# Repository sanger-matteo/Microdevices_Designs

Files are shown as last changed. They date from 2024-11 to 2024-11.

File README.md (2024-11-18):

This repository contains a collection of files used for the creation of microfluidic masks and photolithography work.

## Description of files
This repository includes several scripts used in the study. Below is a brief overview of each:
- **Lithography - Fabrication protocols**:
	- Contains files with different protocols used for the treatment of Si-wafers, photoresist, and fabrication processes for photolithography of microfluidic molds
- **Mask Designs**: if the file are not metric unit, assume *1 unit = 1 micrometer*
	- *Designs:* the *.dwg* and *.dxf* files drawn in CAD that outline the design of different microfluidic designs 
	- *Orders:* similar to "Deasigns", it contains the final *.dwg* and *.dxf* designed used to order and print photolithographhy masks (mostly negative).
- **3D_Nanolithography:**
	- It contains both the *.dwg* and *.stl* of microfluidic molds created via 3D-printing nanolithography.

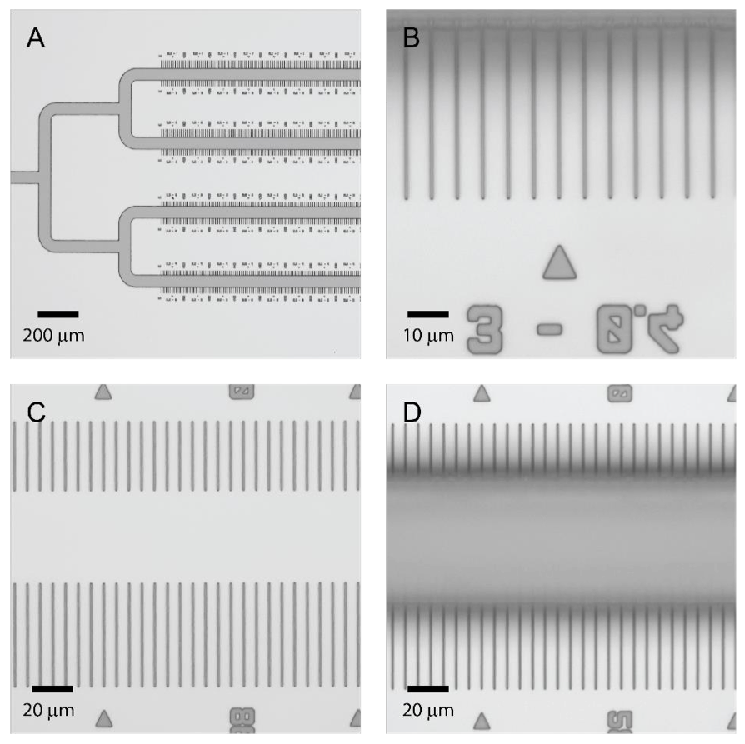
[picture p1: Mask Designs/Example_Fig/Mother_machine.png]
|  |
|---|
| Example 1 - Mother machine Si-Photoresist mold |

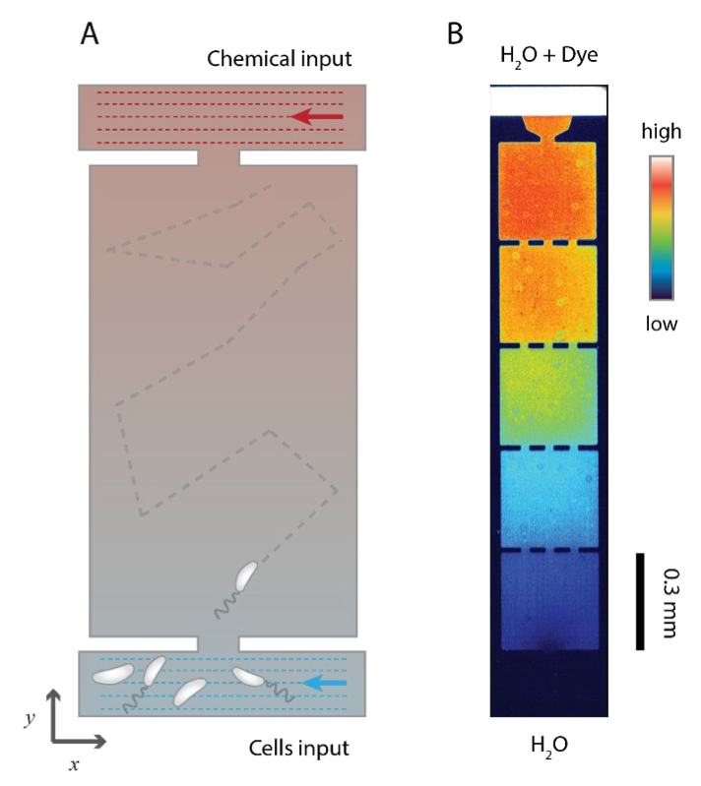
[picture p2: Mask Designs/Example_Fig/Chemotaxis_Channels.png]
|  
|--- |
| Example 2 - Schematic example of a chemotaxis chamber and false color microscopy image of the diffusion and gradient formation of fluorescently labelled molecules |

Some of these files were associated with the following papers (the rest were unpublished or contributed to minor/external collaborations):  
- [Tad Pili Play a Dynamic Role in Caulobacter crescentus Surface Colonization](https://doi.org/10.1128/mbio.01237-19)
- [A Surface-Induced Asymmetric Program Promotes Tissue Colonization by Pseudomonas aeruginosa](https://doi.org/10.1016/j.chom.2018.11.008)
- [Bacteria-on-a-bead: probing the hydrodynamic interplay of dynamic cell appendages during cell separation](https://doi.org/10.1038/s42003-022-04026-z)
- [In situ structure of the Caulobacter crescentus flagellar motor and visualization of binding of a CheY-homolog]( https://doi.org/10.1111/mmi.14525)

Some more specifics can be found in the [thesis](https://edoc.unibas.ch/65308/1/Thesis_v11_edoc.pdf) manuscript.

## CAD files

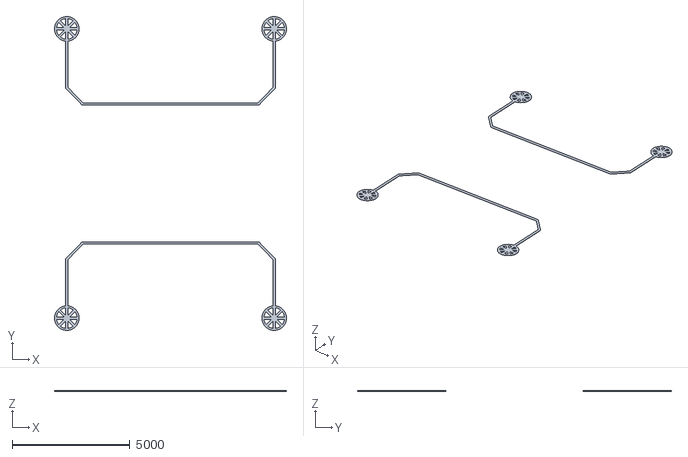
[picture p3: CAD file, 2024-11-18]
Mask Designs/3D_Nanolithography/MGD_v1_channels_3D.stl
9851.3 x 13325.8 x 50.0

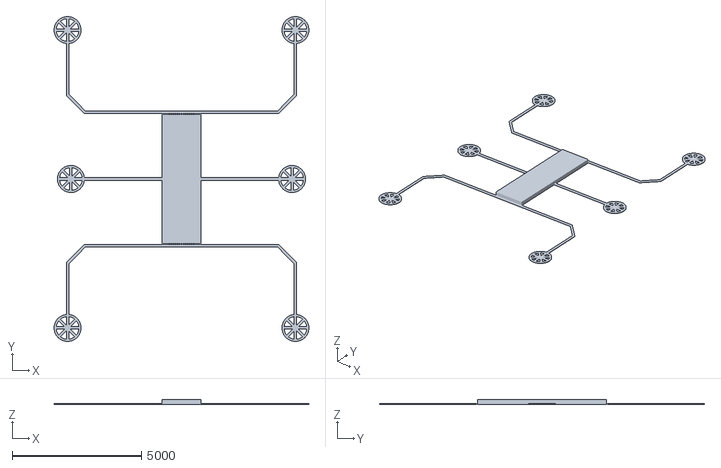
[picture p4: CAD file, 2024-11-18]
Mask Designs/3D_Nanolithography/GD_v1_3D.stl
9859.5 x 12567.7 x 200.0

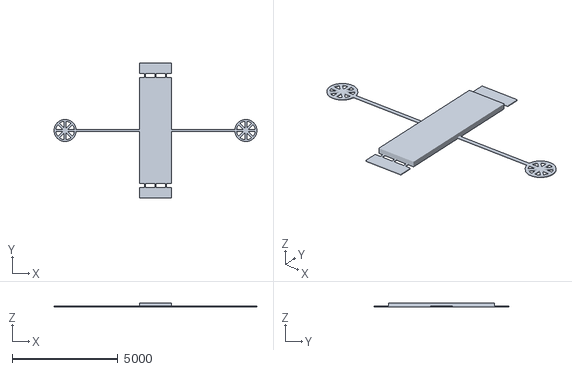
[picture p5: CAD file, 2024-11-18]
Mask Designs/3D_Nanolithography/MGD_v1_chamber_3D.stl
9600.0 x 6400.0 x 200.0

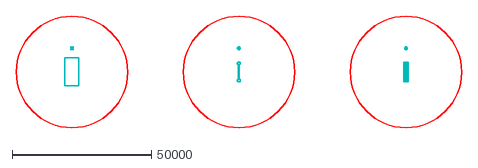
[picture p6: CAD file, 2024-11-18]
Mask Designs/Designs/141211 - MS 4 - Pressure Dev.dxf
160000.0 x 40000.0

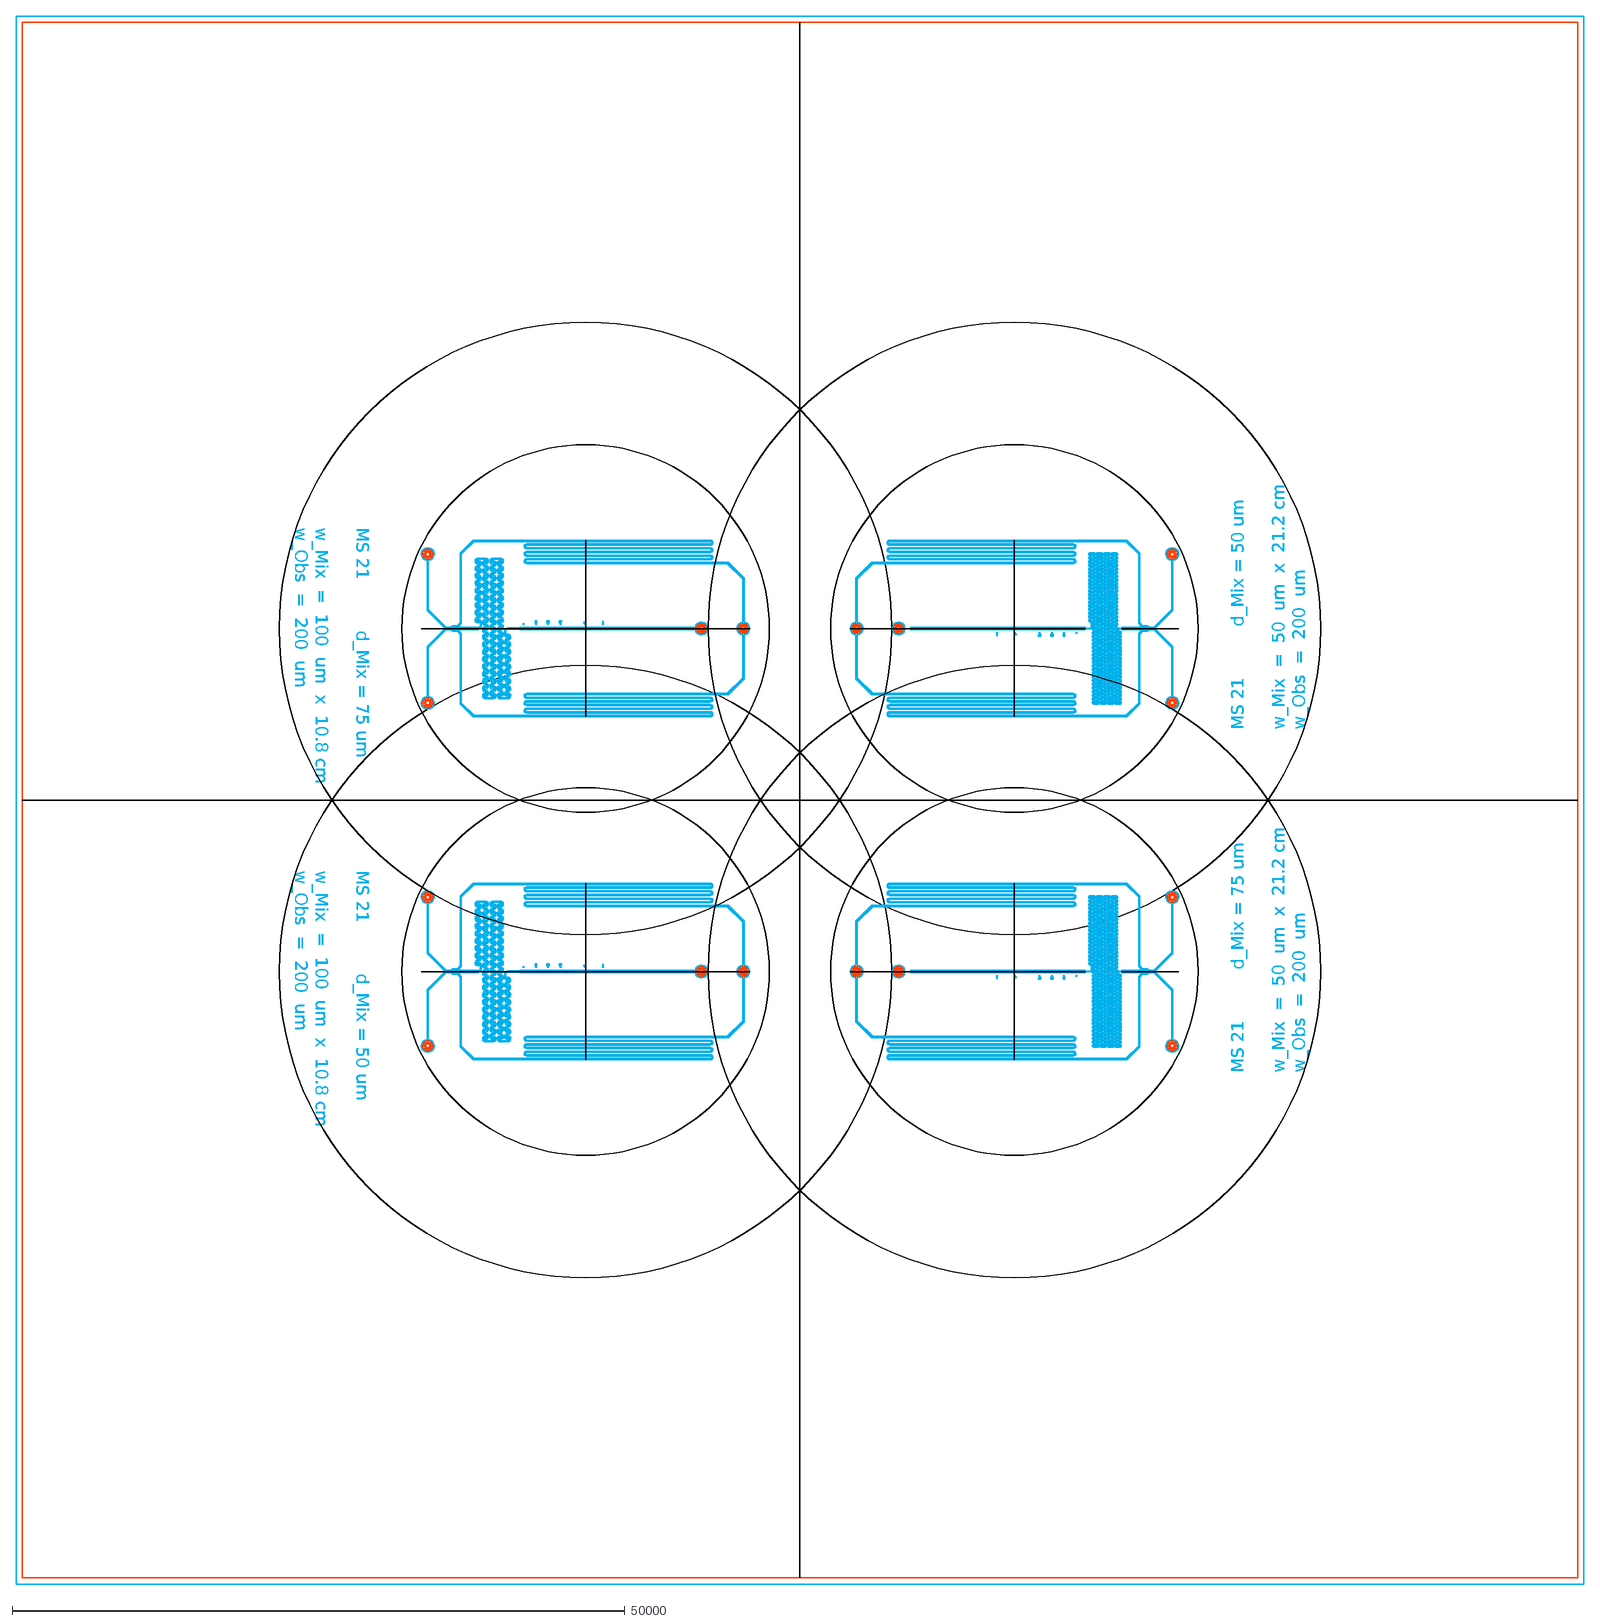
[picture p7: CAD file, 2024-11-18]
Mask Designs/Orders/171206 - Order MS 21 - Switch_Mix.dxf
MS 21 d_Mix = 50 um w_Mix = 100 um x 10.8 cm w_Obs = 200 um
MS 21 d_Mix = 75 um w_Mix = 100 um x 10.8 cm w_Obs = 200 um
MS 21 d_Mix = 50 um w_Mix = 50 um x 21.2 cm w_Obs = 200 um
MS 21 d_Mix = 75 um w_Mix = 50 um x 21.2 cm w_Obs = 200 um

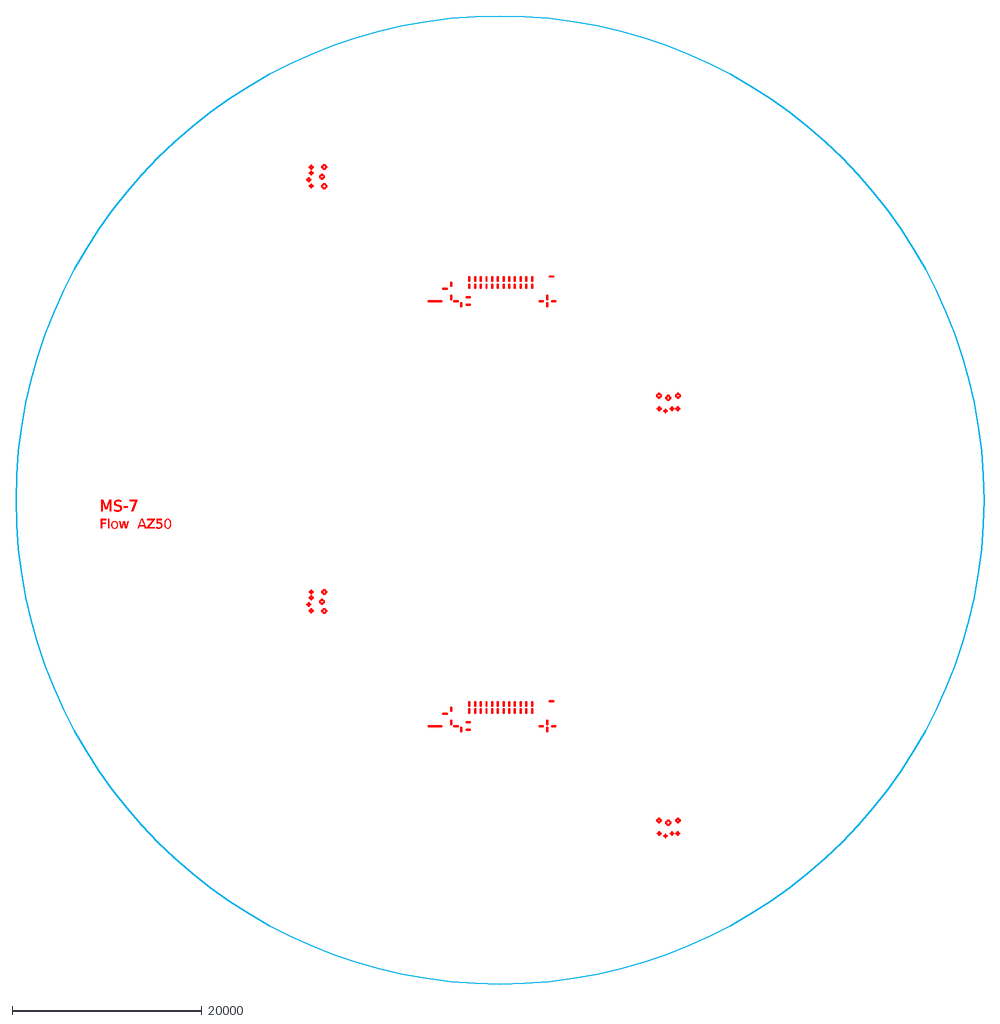
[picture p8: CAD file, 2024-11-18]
Mask Designs/Orders/150708 - Order MS-7 - 2 positive- UniBas - Sangermani.dxf
MS-7 Flow AZ50

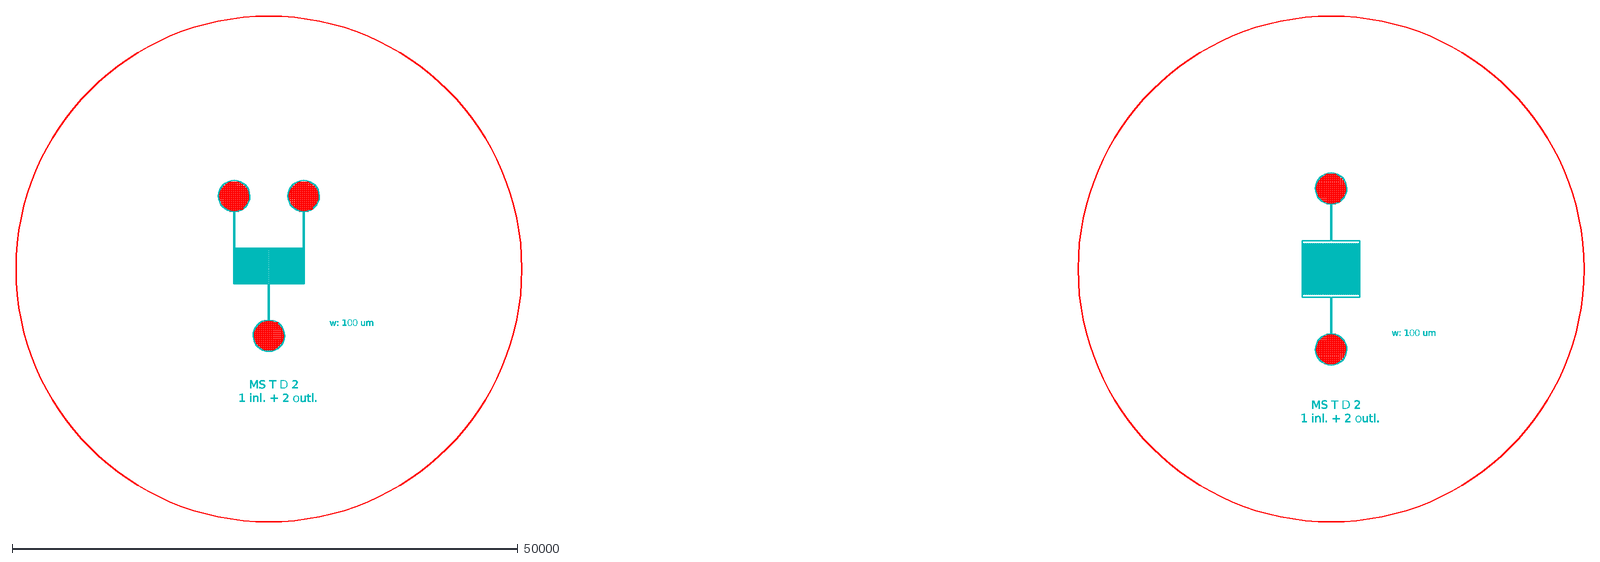
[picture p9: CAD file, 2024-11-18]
Mask Designs/Orders/141007 - Order MS 3 - UniBas - Sangermani.dxf
w: 100 um
MS T D 2 1 inl. + 2 outl.

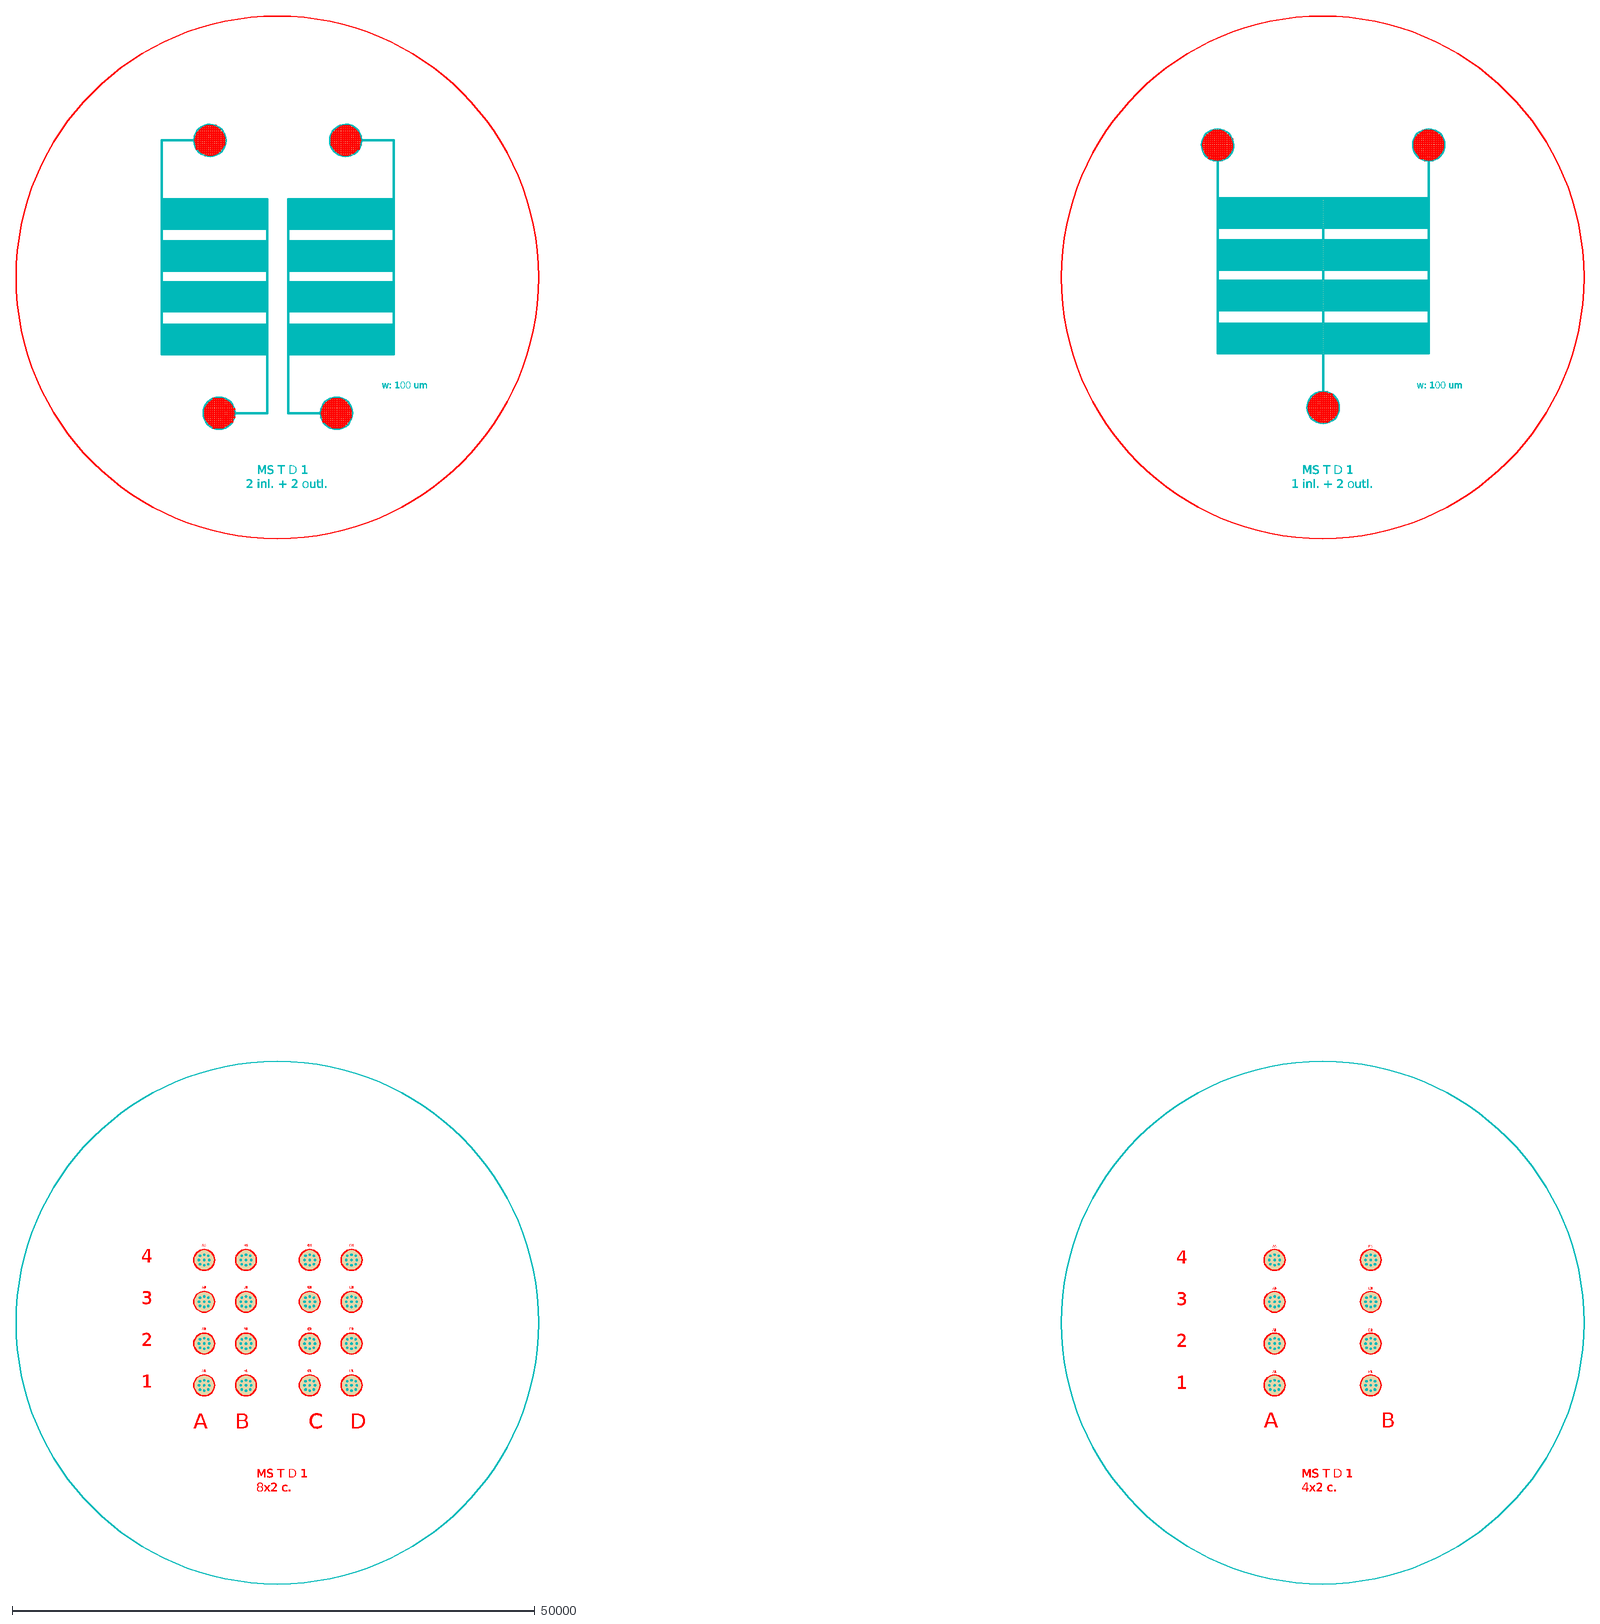
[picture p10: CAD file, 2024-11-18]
Mask Designs/Orders/140516 - Order MS 1 - UniBase - Sangermani.dxf
1
2
3
4
A
B
A1
A2
A3
A4
B4
B3
B2
B1
C
D
C1
C2
C3
C4
D4
D3
D2
D1
w: 100 um
MS T D 1 8x2 c.
MS T D 1 4x2 c.
MS T D 1 2 inl. + 2 outl.
MS T D 1 1 inl. + 2 outl.

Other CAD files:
Mask Designs/Orders/180709 - FW2_GDv2-4_MGDv1.dwg
Mask Designs/Designs/170628 - MS 17 - Switch_Flow_Channel.dwg
Mask Designs/Designs/160316 - MS 15 - Generation_Dev_1.dwg
Mask Designs/Orders/170111 - Order MS 16.2 - Mother Machine Caulo 2.dwg
Mask Designs/Designs/150811 - MS 9-12 - FAC-Counter.dwg
Mask Designs/Orders/160707 - Order MS 13-15 - Positive.dwg
Mask Designs/Designs/160316 - MS 13 - Pusher channel.dwg
Mask Designs/Designs/180704 - MothMach_3D - 2D.dwg
Mask Designs/Designs/171206 - MS 20 - Single_Layer_Valve.dwg
Mask Designs/3D_Nanolithography/GD_v1_3D.dwg
Mask Designs/3D_Nanolithography/MGD_v1_chamber_3D.dwg
Mask Designs/3D_Nanolithography/MGD_v1_channels_3D.dwg
Mask Designs/Designs/140605 - MS 2 - Sangermani Order Final - Chromium.dwg
Mask Designs/Designs/150702 - MS 7 - Swarmer_Attachment_Dev.dwg
Mask Designs/Designs/150806 - MS 6 - Mixing_Flow_Channel.dwg
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

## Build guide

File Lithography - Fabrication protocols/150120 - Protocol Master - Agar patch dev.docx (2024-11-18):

# Master: Agar patch device (Isa 3)

Clean :

- ddH2O
- Acetone
- Sonication
- Dehydration ( 15 min @ 120°C )

Spin :

- HTexture = about 120 μm
- Photoresistor: negative Su-3025; was old (2011) and almost finished

We cannot build up 120 μm in one spin, thus we will do two consecutives ones, with soft baking in between to harden a bit first layer and avoid too have it modified by second spin.

+60 μm | Speed | ramp | Time
0° | 500 rpm | 1 | 10 s
1° | 1000 rpm | 8 | 30 s

Soft Bake 1 : t = 15 min

+60 μm | Speed | ramp | Time
0° | 500 rpm | 1 | 10 s
1° | 1000 rpm | 8 | 30 s

Soft Bake 2 : t = 40 min

Exposure : E = 250 [mJ/cm^2] I =

≈ 11 s

Post Bake :

65°C | ramp | 95°C
1 min | | 5 min

Develop : t = 20 min Hard Baking : about 25 min @ 200°C

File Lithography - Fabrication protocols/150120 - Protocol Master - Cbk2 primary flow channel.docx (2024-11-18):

# Master: Cbk2 device (Primary flow channel of Isa)

Clean :

- ddH2O
- Acetone
- (Sonication, 10 min)
- Dehydration ( 15 min @ 120°C )

Spin :

- HTexture 2 = 15 μm
- HTexture 1 = 8 μm
- Photoresistor: negative Su-3010

+60 μm | Speed | ramp | Time
0° | 500 rpm | 1 | 10 s
1° | 5000 rpm (8 um) 1000 rpm (15 um) | 1 | 30 s

Soft Bake : 1 min @ 65°C + 10 min @ 95°C

Exposure : E20 = 200 [mJ/cm^2] ≈ 9 s

E15 = 150 [mJ/cm^2] ≈ 7 s

Post Bake :

65°C | ramp | 95°C
1 min | | 100 s 5 min

Develop : t = 6 min Hard Baking : about 10 min @ 200°C

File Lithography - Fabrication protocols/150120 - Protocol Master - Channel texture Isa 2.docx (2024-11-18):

# Master: small Channels (Isa 2)

Clean :

- ddH2O
- Acetone
- (Sonication, 10 min)
- Dehydration ( 15 min @ 120°C )

Spin :

- HTexture 2 = 22 μm
- Photoresistor: negative Su-3010

| Speed | ramp | Time
0° | 500 rpm | 1 | 10 s
1° | 1000 rpm | 1 | 30 s

Soft Bake : 1 min @ 65°C + 10 min @ 95°C

Exposure : E22 = 200 [mJ/cm^2] ≈ 8 s

Post Bake :

65°C | ramp | 95°C
1 min | | 4 min

Develop : t = 5-6 min Hard Baking : about 15 min @ 200°C

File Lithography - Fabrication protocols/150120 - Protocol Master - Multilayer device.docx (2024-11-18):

# Master: Multilayer – Thin Chambers device)

This fabrication is a bit more complicated since we will have to produce two the layer for the master texture and therefore we will employ two different masks. We also need to align between formed layer and subsequent masks.

The Layer 1 is is the texture that will build the Thin Chambers, while Layer 2 is the texture for the Main channel

Clean :

- ddH2O
- Acetone
- (Sonication, 10 min)
- Dehydration ( 15 min @ 120°C )

Spin 1 :

- Hlayer 1 = 1.2 μm or 2.2 μm
- Photoresistor: negative Su-2002

| Speed | ramp | Time
0° | 500 rpm | 1 | 10 s
1° | 5000 rpm (1.2 um) 3000 rpm (2.2 um) | 8 | 30 s

Soft Bake 1 : 1 min @ 65°C + 1 min @ 95°C

Mask 1 Exposure 1 : E1.2 = 2.2 = 60 [mJ/cm^2] ≈ 2.7 s

Post Bake 1 :

65°C | ramp | 95°C
1 min | | 1 min

----------------------------------------------------------------------------------------------------------------------------------------------------------Spin 2 :

- Hlayer 2 = about 20 μm
- Photoresistor: negative Su-3050

| Speed | ramp | Time
0° | 500 rpm | 1 | 10 s
1° | 1000 rpm | 1 | 30 s

Soft Bake 2 : 1 min @ 65°C + 3 min @ 95°C

-------------- Allignment -----------------

Mask 2 Exposure 2 : E20 = 200 [mJ/cm^2] ≈ 7.5 s

Post Bake 2 :

65°C | ramp | 95°C
1 min | | 3.5 min

Develop 2 : t = 4 min

Hard Baking : about 15 min @ 200°C

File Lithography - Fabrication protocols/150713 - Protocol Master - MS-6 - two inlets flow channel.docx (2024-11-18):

# Master: MS-6

Clean :

- ddH2O
- Acetone
- (Sonication, 10 min)
- Dehydration ( 15 min @ 120°C )

Spin :

- HTexture = 15 μm

Photoresistor: negative Su-3010

+60 μm | Speed | ramp | Time
0° | 500 rpm | 1 | 10 s
1° | 1000 rpm (15 um) | 1 | 30 s

Soft Bake : 1 min @ 65°C + 10 min @ 95°C

Exposure : E20 = 200 [mJ/cm^2] ≈ 8.2 s

Post Bake :

65°C | ramp | 95°C
1 min | | 5 min

Develop : t = 6-7 min Hard Baking : about 15 min @ 200°C

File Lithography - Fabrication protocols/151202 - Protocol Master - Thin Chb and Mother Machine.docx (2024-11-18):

# Master: Multilayer – Thin Chamb. and Mother Machine

Layer 1 is the smallest feature. For the thin chambers we do ( 0.4, 0.5, 0.6 ) μm, while for Mother machine we will do ( 0.4 0.5 ) μm.

Layer 2 is the texture for the Main channel, which at 30 μm in height, they will be ~ 60 times bigger than layer 1.

Clean :

- ddH2O
- Acetone
- (Sonication, 10 min)
- Dehydration ( 15 min @ 120°C )

Spin 1 :

- Hlayer 1 = 0.6 μm , 0.5 μm , 0.4 μm
- Photoresistor: negative Su-2000.5

height | | Speed | ramp | Time
all | 0° | 500 rpm | 1 | 10 s
0.6 | 1° | 2200 rpm | 3 | 30 s
0.5 | 2° | 3000 rpm | 3 | 30 s
0.4 | 3° | 3700 rpm | 3 | 30 s

Removal of Edge Bead = this will grant better contact between mask and wafer

Soft Bake 1 : 1 min @ 95°C

Mask 1 Exposure 1 : E = 60 [mJ/cm^2] ≈ s

Post Bake 1 :

65°C | ramp | 95°C
/ | | ~ 90 s

----------------------------------------------------------------------------------------------------------------------------------------------------------Spin 2 :

- Hlayer 2 = about 30 μm
- Photoresistor: negative Su-3025

| Speed | ramp | Time
0° | 500 rpm | 1 | 10 s
1° | 2500 rpm | 3 | 30 s

Soft Bake 2 : 1 min @ 65°C + 12 min @ 95°C

-------------- Allignment -----------------

Mask 2 Exposure 2 : E = 180 [mJ/cm^2] ≈ s

Post Bake 2 :

65°C | ramp | 95°C
1 min | | ~3.5 min

Develop 2 : t = 6 min

Hard Baking : about 20 min @ 180°C

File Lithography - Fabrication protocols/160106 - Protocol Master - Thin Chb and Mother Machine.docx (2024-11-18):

# Master: Multilayer –Mother Machine

Layer 1 is the smallest feature. For the thin chambers we do ( 0.4, 0.5, 0.6 ) μm, while for Mother machine we will do ( 0.4 0.5 ) μm.

Layer 2 is the texture for the Main channel, which at 30 μm in height, they will be ~ 60 times bigger than layer 1.

Clean :

- ddH2O
- Acetone
- (Sonication, 10 min)
- Dehydration ( 15 min @ 120°C )

Spin 1 :

- Hlayer 1 = 1 μm , 0.8 μm
- Photoresistor: negative Su-8 2000.5, 2002

height | | Speed | ramp | Time
all | 0° | 500 rpm | 1 | 10 s
1 (Su-8 2002) | 2° | 6000 rpm | 8 | 30 s

Soft Bake 1 : 1 min @ 65°C + 1+1 min @ 95°C

Removal of Edge Bead = this will grant better contact between mask and wafer

Soft Bake 1 : 1 min @ 65°C

Mask 1 Exposure 1 : E = 70 [mJ/cm^2] ≈ 1.8 s

Post Bake 1 :

65°C | ramp | 95°C
1 min | | ~ 2 min

----------------------------------------------------------------------------------------------------------------------------------------------------------Spin 2 :

- Hlayer 2 = about 10 μm
- Photoresistor: negative Su-3010

| Speed | ramp | Time
0° | 500 rpm | 1 | 10 s
1° | 3000 rpm | 8 | 30 s

Soft Bake 2 : 1 min @ 65°C + 3 min @ 95°C + 1 min @ 65°C

Edge Bead removal: thin stream of developer of the edge, while spinning at 750 rpm

Soft Bake 2 : ~ 2 min @ 65°C
[allow reflow and drying, so that photoresistor is not steaky and it is easy to do mask alignment]

-------------- Allignment -----------------

Mask 2 Exposure 2 : E = 180 [mJ/cm^2] ≈ 4.2 s

Post Bake 2 :

65°C | ramp | 95°C
1 min | | ~2-3 min

Develop 2 : t = 5 min

Hard Baking : about 20 min @ 180°C [ramp up, about 10 degrees per min, and down]

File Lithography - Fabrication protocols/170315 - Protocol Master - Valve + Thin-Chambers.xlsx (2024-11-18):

 | Master |  |  | Valve + Thin-Chamb
 | Device which consist of one Main Channel, height 15 um, and Thin Chambers, height ~1 um.
 | The access to chambers has valves to regulate them, height 23 um
 | INFO
 | Layer: |  | 1st | 2nd | 3rd |  | Mask(s) : | JW_01
 | Thickness [um] : |  | 23 | 1 | 25 |  |  | Valve + Thin-Chamb
 | Photoresistor(s) : |  | AZ50 XT | 2000.5 | 3010
 | Clean |  | Sonicate : |  | Wash: | H2O | Acetone | IPA | water | N2
 |  |  | Dehydration : |  | 150° C
 |  |  |  |  | 5 | [min]
 |  |  |  |  | Coat and let sit ~ 30 sec
 | Priming |  | HMDS |  | Spin at 6000 rpm for 30 s
 |  |  |  |  | Bake 100-150 °C, 1-3 min
 | Spin | Height : | 23 | [um] |  | Speed |  | ramp | time
 |  | AZ50 |  |  | 0° | 500 | [rpm] | 5 | 10 s
 |  |  |  |  | 1° | 2700 | [rpm] | 5 | 30 s | (20s)
 |  |  |  |  | 1° | 4500 | [rpm] | 1 | 1 s
 | Rehydr 1 | Let sit on level surface for 10 min. Rehydration an levelling/setting
 | SB |  |  |  |  |  | 112 °C |  |  |  |  | TOT time
 |  |  |  |  |  |  | 3 | [min] |  |  |  | 1.175 | h
 |  |  | 65 °C |  |  |  |  |  |  |  |  | + 3 min
 |  |  | Start | [min] | ramp: | 240 °C/h |  |  | cool |  |  | + cooling
 | Rehydr 2 | Let sit on level surface for 2 h. Rehydration an levelling/setting
 | EXP |  | Dose : |  | XYZ | [mJ/cm2] |  |  | time
 | I-lines |  |  |  |  |  |  | = | 200 [s]
 |  |  | Intensity : |  |  | [W] |  | multistep exposure: |  | (4x) 20 s ON, 30 s OFF
 | ! ! ! ---------------------------- NO PostBake ---------------------------- ! ! !
 | DEV | immediately develop after exposure!
 | dilute developer | Develop : |  | 5 | [min] | Agitate |  | NO IPA wash, just mix in Dev.
 | 1 : 3 |  |  | 1 | [min] | Rinse |  | Rinse with H2O and spin dry
 | dH2O : AZ 400K
 | REFLOW |  |  |  |  |  | 200 °C |  |  |  |  | TOT time
 |  |  |  |  |  |  |  | 13 | [h] |  |  | 9 | h
 |  |  | 65 °C |  |  |  |  |  |  |  |  | + 13 h
 |  |  | Start | [min] | ramp: | 15 °C/h |  |  |  | cool: | 15 °C/h | + cooling
Thin Chambers |  | Su8 | 2002
 |  | mix 2002 with 2000.5 to increase viscosity of the first and be able to spin a 1 um layer
 | Spin | Height : | 1 | [um] |  | Speed |  | ramp | time
 |  | 2002 |  |  | 0° | 500 | [rpm] | 1 | 10s
 |  |  |  |  | 1° | 5000 | [rpm] | 5 | 30s
 | SB - a |  |  |  |  | 95 °C
 |  |  |  |  |  |  | 1 | [min]
 |  |  | 65 °C
 |  |  |  | 1 | [min]
 | Edge Bead removal |  | thin stream of developer of the edge, while spinning at 800 rpm
 | SB - b |  | 65 °C
 |  |  |  | 1 | [min]
 | ---------- ALLIGNMENT ----------
 | EXP |  | Dose : |  | 70 | [mJ/cm2] |  |  | time
 |  |  |  |  |  |  |  | = | [s]
 |  |  | Intensity : |  |  | [W]
 | PBE |  |  |  |  | 95 °C
 |  |  |  |  |  |  | 6 + | [min]
 |  |  | 65 °C
 |  |  |  | 1 | [min]
Main Channels |  | Su8 | 3025
 | Spin | Height : | 25 | [um] |  | Speed |  | ramp | time
 |  | 3025 |  |  | 0° | 500 | [rpm] | 1 | 10s
 |  |  |  |  | 1° | 3500 | [rpm] | 5 | 30s
 | SB - a |  |  |  |  |  | 95 °C
 |  |  |  |  |  |  |  | 7 | [min]
 |  |  | 65 °C
 |  |  |  | 1 | [min] | slow ramp
 | Edge Bead removal |  | thin stream of developer of the edge, while spinning at 800 rpm
 | SB - b |  | 65 °C
 |  |  |  | 5 | [min]
 | Mask swap |  | ---------- ALLIGNMENT ----------
 | EXP |  | Dose : |  | 170 | [mJ/cm2] |  |  | time
 |  |  |  |  |  |  |  | = | [s]
 |  |  | Intensity : |  |  | [W]
 | PBE |  |  |  |  |  | 95 °C
 |  |  |  |  |  |  |  | 7 | [min]
 |  |  | 65 °C
 |  |  |  | 1 | [min] | slow ramp
 | DEV |  | cool @ Room Temp: |  | 5 - 10 | [min]
 |  |  | Develop: |  | 6 + | [min] |  | NO IPA wash, just mix in Dev.
 | Hard Bake |  | 140° C | for | 30 | [min]
 |  |  | (lower temp or AZ50 XT reflow again)

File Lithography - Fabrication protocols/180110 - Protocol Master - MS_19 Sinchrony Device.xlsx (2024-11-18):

 | Master |  |  | Synchrony Device
 | Device which consist of one Main Channel, height 25 um
 | The access to chambers has valves to regulate them, height 23 um
 | INFO
 | Layer: |  | 1st | 2nd |  |  | Mask(s) : | MS_19
 | Thickness [um] : |  | 23 | 23 |  |  |  | Valve + Control
 | Photoresistor(s) : |  | AZ50 XT | 3010
 | Clean |  | Sonicate : |  | Wash: | H2O | Acetone | IPA | water | N2
 |  |  | Dehydration : |  | 150° C
 |  |  |  |  | 5 | [min]
 |  |  |  |  | Coat and let sit ~ 30 sec
 | Priming |  | HMDS |  | Spin at 6000 rpm for 30 s
 |  |  |  |  | Bake 110 °C, 1 min
 | Spin | Height : | 23 | [um] |  | Speed |  | ramp | time
 |  | AZ50 |  |  | 0° | 500 | [rpm] | 5 | 10 s
 |  |  |  |  | 1° | 2700 | [rpm] | 5 | (20s)
 |  |  |  |  | 1° | 4500 | [rpm] | 1 | 1 s
 | Rehydr 1 | Let sit on level surface for 10 min. Rehydration an levelling/setting
 | SB |  |  |  | 115 °C
 |  |  |  |  | 3 | [min]
 |  |  |  |  |  |  | cool
 | Rehydr 2 | Let sit on level surface for 2 h. Rehydration and levelling/setting
 | EXP |  | Dose : |  | --///-- | [mJ/cm2] |  |  | time
 | I-lines |  |  |  |  |  |  | = | 200 [s]
 |  |  | Intensity : |  | --///-- | [W] |  | multistep exposure: |  | (4x) 11 s ON, 30 s OFF
 | ! ! ! ---------------------------- NO PostBake ---------------------------- ! ! !
 | DEV | immediately develop after exposure!
 | dilute developer | Develop : |  | 5 | [min] | Agitate |  | NO IPA wash, just mix in Dev.
 | 1 : 3 |  |  | 1 | [min] | Rinse |  | Rinse with H2O and spin dry
 | dH2O : AZ 400K
 | REFLOW |  |  |  |  |  | 200 °C |  |  |  |  | TOT time
 |  |  |  |  |  |  |  | 13 | [h] |  |  | 9 | h
 |  |  | 65 °C |  |  |  |  |  |  |  |  | + 13 h
 |  |  | Start | [min] | ramp: | 15 °C/h |  |  |  | cool: | 15 °C/h | + cooling
Thin Chambers |  | Su8 | 3010
 | Spin | Height : | ~23 | [um] |  | Speed |  | ramp | time
 |  | 3010 |  |  | 0° | 500 | [rpm] | 1 | 10s
 |  |  |  |  | 1° | 1500 | [rpm] | 5 | 30s
 | SB - a |  |  |  |  |  | 95 °C
 |  |  |  |  |  |  |  | 7 | [min]
 |  |  | 65 °C
 |  |  |  | 1 | [min] | slow ramp
 | Edge Bead removal |  | thin stream of developer of the edge, while spinning at 800 rpm
 | SB - b |  | 65 °C
 |  |  |  | 5 | [min]
 | ---------- ALLIGNMENT ----------
 | EXP |  | Dose : |  | 170 | [mJ/cm2] |  |  | time
 |  |  |  |  |  |  |  | = | [s]
 |  |  | Intensity : |  |  | [W]
 | PBE |  |  |  |  |  | 95 °C
 |  |  |  |  |  |  |  | 7 | [min]
 |  |  | 65 °C
 |  |  |  | 1 | [min] | slow ramp
 | DEV |  | cool @ Room Temp: |  | 5 - 10 | [min]
 |  |  | Develop: |  | 6 + | [min] |  | NO IPA wash, just mix in Dev.
 | Hard Bake |  | 140° C | for | 30 | [min]
 |  |  | (lower temp or AZ50 XT reflow again)

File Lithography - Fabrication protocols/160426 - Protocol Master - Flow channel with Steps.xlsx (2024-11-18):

Master |  |  | Prymary flow channel with steps
 | Device with simply consist of one primary channel , width of 100 um.
Ont top of that we add a discontinuos second layer, in order to create a steps like roof on the ceiling of our channel
INFO
Thickness : | [um] | 1st | 2nd |  | Mask(s) : | MS 10 |  | MS 10
 |  | 15 | 15 |  |  | Clannel |  | Steps
Photoresistor(s) : |  | 3010 | 3010 | ( Su8 )
Clean |  | Sonicate : |  | Wash: | H2O | Acetone | IPA | N2
 |  | Dehydration : |  | 150° C
 |  |  |  | 5 | [min]
Priming |  | HMDS | Will be shown
Spin 1 | Height : | 15 [um] |  |  | Speed |  | ramp | time
 | Su8 | 3010 |  | 0° | 500 | [rpm] | 1 | 10s
 |  |  |  | 1° | 1000 | [rpm] | 3 | 30s
SB 1 |  |  |  |  | 95 °C
 |  |  |  |  |  | 10 | [min]
 |  | 65 °C
 |  |  | 1 | [min]
EXP 1 |  | Dose : |  | 200 | [mJ/cm2] |  |  | time
 |  |  |  |  |  |  | = | [s]
 |  | Intensity : |  |  | [W]
PBE 1 |  |  |  |  | 95 °C
 |  |  |  |  |  | 5 | [min]
 |  | 65 °C
 |  |  | 1 | [min]
Spin 2 | Height : | 15 [um] |  |  | Speed |  | ramp | time
 | Su8 | 3010 |  | 0° | 500 | [rpm] | 1 | 10s
 |  |  |  | 1° | 1000 | [rpm] | 3 | 30s
SB 2 a |  |  |  |  | 95 °C
 |  |  |  |  |  | 10 | [min]
 |  | 65 °C
 |  |  | 1 | [min]
Edge Bead removal |  | thin stream of developer of the edge, while spinning at 800 rpm
SB 2 b |  | 65 °C
 |  |  | 2 - 3 | [min]
Mask swap |  | ---------- ALLIGNMENT ----------
EXP 2 |  | Dose : |  | 200 | [mJ/cm2] |  |  | time
 |  |  |  |  |  |  | = | [s]
 |  | Intensity : |  |  | [W]
PBE 2 |  |  |  |  | 95 °C
 |  |  |  |  |  | 6 | [min]
 |  | 65 °C
 |  |  | 1 | [min]
DEV |  | cool @ Room Temp : |  | 5 - 10 | [min]
 |  | Develop : |  | 6 | [min]
HB |  | 200° C | for | 20 | [min]

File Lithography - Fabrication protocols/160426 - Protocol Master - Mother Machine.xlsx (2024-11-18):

Master |  |  | Mother Machine
 | Device with simply consist of one primary channel , width of 50 um and height 15 um.
At sides are thin channels of width around 1 um and height of about 0.9 - 1 um
INFO
Thickness : | [um] | 1st | 2nd |  | Mask(s) : | Moter machine
 |  | 0.6 | 20
Photoresistor(s) : |  | 2000.5 | 3010 | ( Su8 )
Clean |  | Sonicate : |  | Wash: | H2O | Acetone | IPA | N2
 |  | Dehydration : |  | 150° C
 |  |  |  | 5 | [min]
Priming |  | HMDS | Not necessary
 | mix 2002 with 2000.5 to increase viscosity of the first and be able to spin a 1 um layer
Spin 1 | Height : | 0... [um] |  |  | Speed |  | ramp | time
2000.5 |  |  |  | 0° | 500 | [rpm] | 1 | 10s
 |  |  | 0.7 | 1° | 1500 | [rpm] | 3 | 30s
 |  |  | 0.6 | 1° | 2000 | [rpm] | 3 | 30s
 |  |  | 0.7 | 1° | 2500 | [rpm] | 3 | 30s
SB 1 |  |  |  |  | 95 °C
 |  |  |  |  |  | 1 | [min]
 |  | 65 °C
 |  |  | 1 | [min]
EXP 1 |  | Dose : |  | 62 | [mJ/cm2] |  |  | time
 |  |  |  |  |  |  | = | [s]
 |  | Intensity : |  |  | [W]
PBE 1 |  |  |  |  | 95 °C
 |  |  |  |  |  | 1 | [min]
 |  | 65 °C |  |  |  | make it short, just to solidify a bit
 |  |  | 30 | [s]
Spin 2 | Height : | 15 [um] |  |  | Speed |  | ramp | time
 | Su8 | 3010 |  | 0° | 500 | [rpm] | 1 | 10s
 |  |  |  | 1° | 1000 | [rpm] | 3 | 30s
SB 2 a |  |  |  |  | 95 °C
 |  |  |  |  |  | 7 | [min]
 |  | 65 °C |  |  |  | make it short, just to solidify a bit
 |  |  | 1 | [min]
Edge Bead removal |  | thin stream of developer of the edge, while spinning at 800 rpm
SB 2 b |  | 65 °C
 |  |  | 2 - 3 | [min]
Mask swap |  | ---------- ALLIGNMENT ----------
EXP 2 |  | Dose : |  | 200 | [mJ/cm2] |  |  | time
 |  |  |  |  |  |  | = | [s]
 |  | Intensity : |  |  | [W]
PBE 2 |  |  |  |  | 95 °C
 |  |  |  |  |  | 6 | [min]
 |  | 65 °C
 |  |  | 1 | [min]
DEV |  | cool @ Room Temp : |  | 5 - 10 | [min]
 |  | Develop : |  | 6 | [min] |  | NO IPA wash, just mix in Dev.
HB |  | 200° C | for | 20 | [min]

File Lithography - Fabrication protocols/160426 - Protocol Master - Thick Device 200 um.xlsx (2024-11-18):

Master |  |  | Thick device - 200 um
INFO
Thickness : | [um] | 1st |  |  | Mask(s) :
 |  | 200
Photoresistor(s) : |  | 2100 | ( Su8 )
Clean |  | Sonicate : |  | Wash: | H2O | Acetone | IPA | N2
 |  | Dehydration : |  | 150° C
 |  |  |  | 5 | [min]
Priming |  | HMDS | Will be shown
Spin 1 | Height : | 200 [um] |  |  | Speed |  | ramp | time
 | Su8 | 2100 |  | 0° | 500 | [rpm] | 1 | 10s
 |  |  |  | 1° | 1500 | [rpm] | 3 | 30s
SB |  |  |  |  |  |  | ramp | 95 °C
 |  |  |  | ramp | 65 °C |  |  | 90 | [min]
 |  | 40° C |  |  | 30 | [min]
 |  | 10 | [min]
EXP |  | Dose : |  | 325 | [mJ/cm2] |  |  | time
 |  |  |  |  |  |  | = | [s]
 |  | Intensity : |  |  | [W]
PBE |  |  |  |  |  |  | ramp | 95 °C
 |  |  |  | ramp | 65 °C |  |  | 15 | [min]
 |  | 40° C |  |  | 10 | [min]
 |  | 5 | [min]
DEV |  | cool @ Room Temp : |  | 5 - 10 | [min]
 |  | Develop : |  | 15 - 20 | [min] |  | No IPA !!!
HB |  | 200° C | for | 20 | [min]

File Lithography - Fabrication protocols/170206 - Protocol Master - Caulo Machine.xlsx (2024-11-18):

Master |  |  | Caulobacter Machine
 | Device with simply consist of one primary channel , width of 50 um and height 15 um.
At sides are thin channels of width <0.8 um and height of about 0.7 - 0.5 um
INFO
Thickness : | [um] | 1st | 2nd |  | Mask(s) : | Caulo machine
 |  | 0.5 | 20
Photoresistor(s) : |  | 2000.5 | 3010 | ( Su8 )
Clean |  | Sonicate : |  | Wash: | H2O | Acetone | IPA | water | N2
 |  | Dehydration : |  | 150° C
 |  |  |  | 5 | [min]
 |  |  |  | Coat and let sit ~ 30 sec
Priming |  | HMDS |  | Spin at 6000 rpm for 30 s
 |  |  |  | Bake 100-150 °C, 1-3 min
 | mix 2002 with 2000.5 to increase viscosity of the first and be able to spin a 1 um layer
Spin 1 | Height : | 0... [um] |  |  | Speed |  | ramp | time
2000.5 |  |  |  | 0° | 500 | [rpm] | 1 | 10s
 |  |  | 0.5 | 1° | 2750 | [rpm] | 5 | 30s
 |  |  |  | 2° | 4500 | [rpm] | 1 | 1 s
Edge Bead removal |  | thin stream of developer of the edge, while spinning at 800 rpm
Clean Wafer |  | ----> clean wafer bottom of any residual photoresist !!!
SB - a |  |  |  |  | 95 °C
 |  |  |  |  |  | 1 | [min]
 |  | 65 °C
 |  |  | 1 | [min]
Clean Mask |  | Clean mask and air blow and microscope vacuum chulk
EXP 1 |  | Dose : |  | 60 | [mJ/cm2] |  |  | time
 |  |  |  |  |  |  | = | [s]
 |  | Intensity : |  |  | [W]
SB - a |  |  |  |  | 95 °C
 |  |  |  |  |  | 1 | [min]
 |  | 65 °C
 |  |  | 1 | [min]
DEV |  | cool @ Room Temp : |  | 5 - 10 | [min]
 |  | Develop : |  | 6 + | [min] |  | NO IPA wash, just mix in Dev.
EXPOSURE
Spin 2 | Height : | 15 [um] |  |  | Speed |  | ramp | time
 | Su8 | 3010 |  | 0° | 500 | [rpm] | 1 | 10s
 |  |  |  | 1° | 1000 | [rpm] | 3 | 30s
SB 2 a |  |  |  |  | 95 °C
 |  |  |  |  |  | 6 | [min]
 |  | 65 °C |  |  |  | make it short, just to solidify a bit
 |  |  | 1 | [min]
Edge Bead removal |  | thin stream of developer of the edge, while spinning at 800 rpm
SB 2 b |  | 65 °C
 |  |  | 6 | [min]
Mask swap |  | ---------- ALLIGNMENT ----------
EXP 2 |  | Dose : |  | 200 | [mJ/cm2] |  |  | time
 |  |  |  |  |  |  | = | [s]
 |  | Intensity : |  |  | [W]
PBE 2 |  |  |  |  | 95 °C
 |  |  |  |  |  | 6 + | [min]
 |  | 65 °C
 |  |  | 1 | [min]
DEV |  | cool @ Room Temp : |  | 5 - 10 | [min]
 |  | Develop : |  | 6 | [min] |  | NO IPA wash, just mix in Dev.
HB |  | 200° C | for | 20 | [min]

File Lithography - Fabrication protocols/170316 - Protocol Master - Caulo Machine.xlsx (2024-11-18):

 | Master |  |  | Caulobacter Machine
 |  | Device with simply consist of one primary channel , width of 50 um and height 15 um.
 | At sides are thin channels of width <0.7 um and height of about 0.55 um
 | INFO
 | Thickness : | [um] | 1st | 2nd |  | Mask(s) : | Caulo machine
 |  |  | 0.55 | 15
 | Photoresistor(s) : |  | 2000.5 | 3010 | ( Su8 )
Microchannels |  | Su8 | 2000.5
 | Clean |  | Sonicate : |  | Wash: | H2O | Acetone | IPA | water | N2
 |  |  | Dehydration : |  | 150° C
 |  |  |  |  | 5 | [min]
 |  |  |  |  | Coat and let sit ~ 10 sec
 | Priming | MCC Prime 80/20 |  |  | Spin @ 3000-5000 rpm for 20-30 s (untill interference fringes disappear)
 |  |  |  |  | Bake 110 °C, 1-3 min
 |  | mix 2002 with 2000.5 to increase viscosity of the first and be able to spin a 1 um layer
 | Spin 1 | Height : | 0.55 [um] |  |  | Speed |  | ramp | time
 | 2000.5 |  |  |  | 0° | 500 | [rpm] | 1 | 10s
 |  |  |  | 0.5 | 1° | 2750 | [rpm] | 5 | 30s
 | Clean Wafer |  | ----> clean wafer bottom. Do not tilt wafer or it reflow !!!
 | SB - a |  |  |  |  | 95 °C
 |  |  |  |  |  |  | 1 | [min]
 |  |  | 65 °C
 |  |  |  | 1 | [min]
 | Edge Bead removal |  | thin stream of developer of the edge, while spinning at 800 rpm
 | Clean Mask |  | Clean mask and air blow and microscope vacuum chulk. Do not tilt wafer or it reflow !!!
 | EXP 1 |  | Dose : |  | 60 | [mJ/cm2] |  |  | time
 |  |  |  |  |  |  |  | = | 1.5 or 1.4 [s]
 |  |  | Intensity : |  | 30 | [W]
 | SB - a |  |  |  |  | 95 °C
 |  |  |  |  |  |  | 1 | [min]
 |  |  | 65 °C
 |  |  |  | 1 | [min]
 | DEV |  | cool @ Room Temp : |  | 5 - 10 | [min]
 |  |  | Develop : |  | 1 : 30 | [min] |  | NO IPA wash, just mix in Dev.
Main Channels |  | Su8 | 3010
 | Spin | Height : | 15 | [um] |  | Speed |  | ramp | time
 |  | 3010 |  |  | 0° | 500 | [rpm] | 1 | 10s
 |  |  |  |  | 1° | 1500 | [rpm] | 5 | 30s
 | SB - a |  |  |  |  |  | 95 °C
 |  |  |  |  |  |  |  | 5 | [min]
 |  |  | 65 °C
 |  |  |  | 1 | [min] | slow ramp
 | Edge Bead removal |  | thin stream of developer of the edge, while spinning at 800 rpm
 | SB - b |  |  |  |  | 95 °C
 |  |  |  |  |  | 5 | [min]
 |  |  |  | 65 °C
 |  |  |  | 2 | [min]
 | Mask swap |  | ---------- ALLIGNMENT ----------
 | EXP |  | Dose : |  | 170 | [mJ/cm2] |  |  | time
 |  |  |  |  |  |  |  | = | 5.5 [s]
 |  |  | Intensity : |  | 30 | [W]
 | PBE |  |  |  |  | 95 °C
 |  |  |  |  |  |  | 4 | [min]
 |  |  | 65 °C
 |  |  |  | 1 | [min]
 | DEV |  | cool @ Room Temp: |  | 5 - 10 | [min]
 |  |  | Develop: |  | 6 | [min] |  | NO IPA wash, just mix in Dev.
 | Hard Bake |  | 200° C | for | 25 | [min]

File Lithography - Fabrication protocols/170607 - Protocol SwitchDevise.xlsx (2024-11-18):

Master |  |  | Caulobacter Machine
 | Device with simply consist of primary channel , width of 100 um and height 20 um.
INFO
Thickness : | [um] | 1.1 | 1.2 |  | Mask(s) : | Switch Device
 |  | 20 | 20
Photoresistor(s) : |  | 3010 | 3025 | ( Su8 )
Clean |  | Sonicate : |  | Wash: | H2O | Acetone | IPA | water | N2
 |  | Dehydration : |  | 150° C
 |  |  |  | 5 | [min]
Priming
Spin | Height : | 20 [um] |  |  | Speed |  | ramp | time
 |  |  | 3010 | 0° | 500 | [rpm] | 1 | 10s
 |  |  |  | 1.1 | 1000 | [rpm] | 3 | 30s
 |  |  | 3025 | 1.2 | 5000 | [rpm] | 5 | 30s
 | WAIT | 10 to 20 min that on flat surface, to allow reflow and even the surface
Clean Wafer |  | ----> clean wafer bottom of any residual photoresist !!!
SB |  |  |  |  |  | 95 °C
 |  |  |  |  |  |  | 10+ | [min]
 |  | 65 °C
 |  |  | 1 | [min] | ramp
Clean Mask |  | Clean mask and air blow and microscope vacuum chulk
EXPOSE |  | Dose : |  | 150 | [mJ/cm2] |  |  | time
 |  |  |  |  |  |  | = | [s]
 |  | Intensity : |  |  | [W]
PEB |  |  |  |  |  | 95 °C
 |  |  |  |  |  |  | 4 | [min]
 |  | 65 °C
 |  |  | 1 | [min] | ramp
DEV |  | cool @ Room Temp : |  | 5 | [min]
 |  | Develop : |  | 5-6 | [min] |  | NO IPA wash, just mix in Dev.
HB |  | Hard Bake (cure) : |  | 20-30 | [min] |  | 150-200 °C

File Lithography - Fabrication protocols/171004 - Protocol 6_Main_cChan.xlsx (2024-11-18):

Master |  |  | 6 parallel Main Channel - close obs. area
 | Device with simply consist of 6 parallel primary channels, with width of 100 or 200 um and height 35 and 50 um
INFO
Thickness : | [um] | 1.1 | 1.2 |  | Mask(s) : | MS_18
 |  | 35 | 50
Photoresistor(s) : |  | 3025 | 3025 | ( Su8 )
Clean |  | Sonicate : |  | Wash: | H2O | Acetone | IPA | water | N2
 |  | Dehydration : |  | 150° C
 |  |  |  | 5 | [min]
Priming
Spin | Height : |  |  |  | Speed |  | ramp | time
 |  |  |  | 0° | 500 | [rpm] | 1 | 10s
 |  | 35 [um] |  | 1.1 | 2100 | [rpm] | 3 | 30s
 |  | 50 [um] |  | 1.2 | 1400 | [rpm] | 5 | 30s
 | WAIT | 10 to 20 min that on flat surface, to allow reflow and even the surface
Clean Wafer |  | ----> clean wafer bottom of any residual photoresist !!!
SB |  |  |  |  |  | 95 °C
 |  |  |  |  |  |  | 12 / 15 | [min]
 |  | 65 °C
 |  |  | 1 | [min] | ramp
Clean Mask |  | Clean mask and air blow and microscope vacuum chulk
EXPOSE |  | Dose : |  | 200 | [mJ/cm2] |  |  | time
 |  |  |  |  |  |  | = | [s]
 |  | Intensity : |  |  | [W]
PEB |  |  |  |  |  | 95 °C
 |  |  |  |  |  |  | 5 | [min]
 |  | 65 °C
 |  |  | 1 | [min] | ramp
DEV |  | cool @ Room Temp : |  | 5 | [min]
 |  | Develop : |  | 8 | [min] |  | NO IPA wash, just mix in Dev.
HB |  | Hard Bake (cure) : |  | 20-30 | [min] |  | 150-200 °C

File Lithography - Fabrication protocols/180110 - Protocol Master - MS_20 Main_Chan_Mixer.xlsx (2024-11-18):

Master |  |  | MS19-20 - Mixing 2 Inlets + channel
 | Device with simply consist of 6 parallel primary channels, with width of 100 or 200 um and height 25 and 50 um
INFO
Thickness : | [um] | 1.2 |  |  | Mask(s) : | MS_20
 |  | 50
Photoresistor(s) : |  | 3025 | ( Su8 )
Clean |  | Sonicate : |  | Wash: | H2O | Acetone | IPA | water | N2
 |  | Dehydration : |  | 150° C
 |  |  |  | 5 | [min]
 |  |  |  | Coat and let sit ~ 10 sec
Priming | MCC Prime 80/20 |  |  | Spin @ 3000-5000 rpm for 20-30 s (untill interference fringes disappear)
 |  |  |  | Bake 110 °C, 1-3 min
Spin | Height : |  |  |  | Speed |  | ramp | time
 |  |  |  | 0° | 500 | [rpm] | 1 | 10s
 |  | 25 [um] |  | 1.2 | 4000 | [rpm] | 5 | 30s
 |  | 50 [um] |  | 1.2 | 1400 | [rpm] | 5 | 30s
 | WAIT | 10 to 20 min that on flat surface, to allow reflow and even the surface
Clean Wafer |  | ----> clean wafer bottom of any residual photoresist !!!
SB |  |  |  |  |  | 95 °C
 |  |  |  |  |  |  | 14 [min] | (for 50 um)
 |  | 65 °C |  |  |  |  | 11 [min] | (for 25 um)
 |  |  | 1 | [min] | ramp
Clean Mask |  | Clean mask and air blow and microscope vacuum chulk
EXPOSE |  | Dose : |  | 220 | [mJ/cm2] |  |  | time
 |  |  |  |  |  |  | = | 7.3 [s] |  | for 50 um
 |  | Intensity : |  | 30 | [W] |  |  | 6.6 [s] |  | for 25 um
PEB |  |  |  |  |  | 95 °C
 |  |  |  |  |  |  | 5 | [min]
 |  | 65 °C
 |  |  | 1 | [min] | ramp
DEV |  | cool @ Room Temp : |  | 5 | [min]
 |  | Develop : |  | 8 | [min] |  | NO IPA wash, just mix in Dev.
HB |  | Hard Bake (cure) : |  | 20-30 | [min] |  | 150 °C

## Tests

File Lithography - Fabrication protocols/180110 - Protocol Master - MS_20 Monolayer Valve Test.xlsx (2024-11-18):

 | Master |  |  | Monolayer Valves
 | Device which consist of one Main Channel, height 25 um, and Control Valves, height ~70 um.
 | The access to chambers has valves to regulate them, height ~15 um
 | INFO
 | Layer: |  | 1st | 2nd | 3rd |  | Mask(s) : | MS_20
 | Thickness [um] : |  | 15 | 25 | 70 |  |  | Valve + Thin-Chamb
 | Photoresistor(s) : |  | AZ 40XT | 3010 | 3050
 | Clean |  | Sonicate : |  | Wash: | H2O | Acetone | IPA | water | N2
 |  |  | Dehydration : |  | 150° C
 |  |  |  |  | 5 | [min]
 |  |  |  |  | Coat and let sit ~ 10 sec
 | Priming | MCC Prime 80/20 |  |  | Spin @ 3000-5000 rpm for 20-30 s (untill interference fringes disappear)
 |  |  |  |  | Bake 110 °C, 1-3 min
 | Spin | Height : | ~15 | [um] |  | Speed |  | ramp | time
 |  | AZ 40XT |  |  | 0° | 500 | [rpm] | 5 | 10 s
 |  |  |  |  | 1° | 5000 | [rpm] | 5 | 30 s
 | Rehydr 1 | Let sit on level surface for 10 min. Rehydration an levelling/setting
 | SB |  |  |  |  |  | 110 °C |  |  |  |  | TOT time
 |  |  |  |  |  |  | 5 | [min] |  |  |  | 1.175 | h
 |  |  | 65 °C |  |  |  |  |  |  |  |  | + 3 min
 |  |  | 5 | [min] | ramp: | 240 °C/h |  |  | cool |  |  | + cooling
 | Rehydr 2 | Let sit on level surface for 2 h. Rehydration an levelling/setting
 | EXP |  | Dose : |  | 150 | [mJ/cm2] |  |  | time
 | I-lines |  |  |  |  |  |  | = | [s]
 |  |  | Intensity : |  |  | [W] |  | exposure cycles: |  | (4x) s ON, s OFF
 | ! ! ! ---------------------------- NO PostBake ---------------------------- ! ! !
 | DEV | immediately develop after exposure!
 | dilute developer | Develop : |  | 5 | [min] | Agitate |  | NO IPA wash, just mix in Dev.
 | 1 : 3 |  |  | 1 | [min] | Rinse |  | Rinse with H2O and spin dry
 | dH2O : AZ 400K
 | REFLOW |  |  |  |  |  | 120 °C |  |  |  |  | TOT time
 |  |  |  |  |  |  |  | 2 | [min] |  |  | 3.5 h
 |  |  | 65 °C |  |  |  |  |  |  |  |  | +2 min
 |  |  | Start | [min] | ramp: | 15 °C/h |  |  |  | cool: | 15 °C/h | + cooling
Main Channel |  | Su8 | 3010
 | Spin | Height : | ~25 | [um] |  | Speed |  | ramp | time
 |  | 3010 |  |  | 0° | 500 | [rpm] | 1 | 10s
 |  |  |  |  | 1° | 1200 | [rpm] | 5 | 30s
 | SB - a |  |  |  |  |  | 95 °C
 |  |  |  |  |  |  |  | 7 | [min]
 |  |  | 65 °C
 |  |  |  | 1 | [min] | slow ramp
 | Edge Bead removal |  | thin stream of developer of the edge, while spinning at 800 rpm
 | SB - b |  | 65 °C
 |  |  |  | 5 | [min]
 | ---------- ALLIGNMENT ----------
 | EXP |  | Dose : |  | 170 | [mJ/cm2] |  |  | time
 |  |  |  |  |  |  |  | = | [s]
 |  |  | Intensity : |  |  | [W]
 | PBE |  |  |  |  |  | 95 °C
 |  |  |  |  |  |  |  | 5 | [min]
 |  |  | 65 °C
 |  |  |  | 1 | [min] | slow ramp
 | DEV |  | cool @ Room Temp: |  | 5 - 10 | [min]
 |  |  | Develop: |  | 6 + | [min] |  | NO IPA wash, just mix in Dev.
Valve Control |  | Su8 | 3050
 | Spin | Height : | 70 | [um] |  | Speed |  | ramp | time
 |  | 3025 |  |  | 0° | 500 | [rpm] | 1 | 10s
 |  |  |  |  | 1° | 1900 | [rpm] | 5 | 30s
 | SB - a |  |  |  |  |  | 95 °C
 |  |  |  |  |  |  |  | 25 | [min]
 |  |  | 65 °C
 |  |  |  | 1 | [min] | slow ramp
 | Edge Bead removal |  | thin stream of developer of the edge, while spinning at 800 rpm
 | SB - b |  | 65 °C
 |  |  |  | 10 | [min]
 | Mask swap |  | ---------- ALLIGNMENT ----------
 | EXP |  | Dose : |  | 220 | [mJ/cm2] |  |  | time
 |  |  |  |  |  |  |  | = | [s]
 |  |  | Intensity : |  |  | [W]
 | PBE |  |  |  |  |  | 95 °C
 |  |  |  |  |  |  |  | 7 | [min]
 |  |  | 65 °C
 |  |  |  | 1 | [min] | slow ramp
 | DEV |  | cool @ Room Temp: |  | 5 - 10 | [min]
 |  |  | Develop: |  | 15 | [min] |  | NO IPA wash, just mix in Dev.
 | Hard Bake |  | 100° C | for | 120 | [min]
 |  |  | (lower temp or AZ50 XT reflow again)
